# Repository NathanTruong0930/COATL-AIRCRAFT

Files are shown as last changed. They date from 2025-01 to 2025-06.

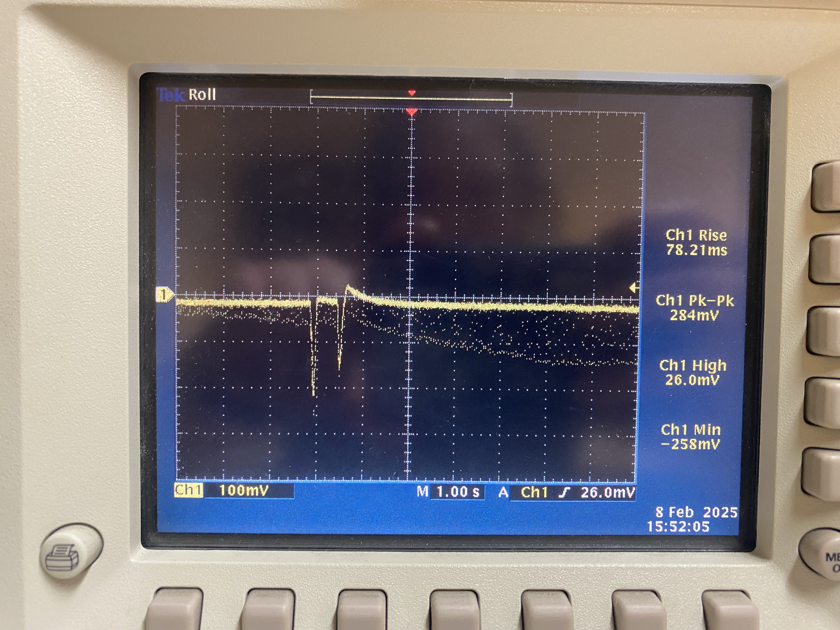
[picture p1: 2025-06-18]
Test Data/gain1_2chargesagain.jpg

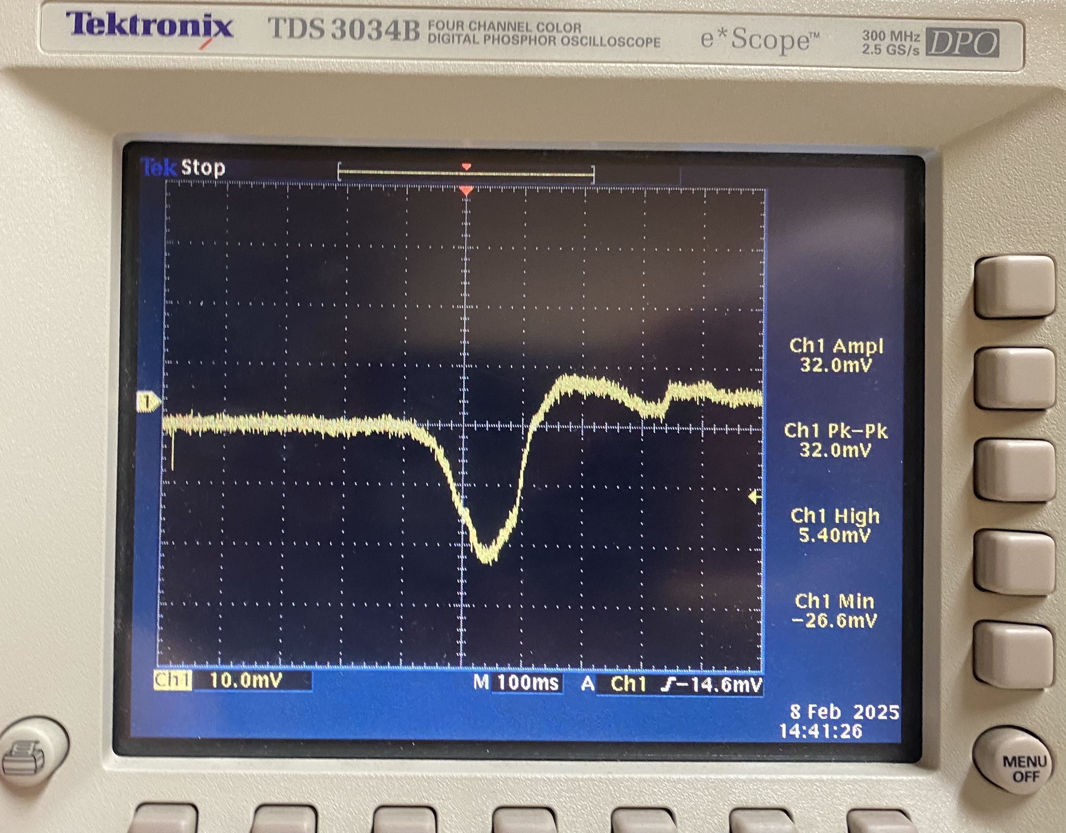
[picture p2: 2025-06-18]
Test Data/gain1_1charge_notcleanestpour.jpg

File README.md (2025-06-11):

# COATL-AIRCRAFT

## Team 3 Members:
- Felix Moss
- Annika Boyd
- Eisa Alsharifi
- Nathan Truong

---

### Project: Electrostatic Dust Analyzer

This repository contains code and resources for the **Electrostatic Dust Analyzer** project developed as part of the PSU Capstone program. This project utilizes a QT PY ESP32 Development Board to interpret current measurements taken from dust particles for use in determining air conditions. 

---

### Key Features

1. **Real-Time Detection of Charged Particles**

    Detects volcanic ash, mineral dust, and wildfire smoke using induced charge measurements.

2. **Electrostatic Sensing Technology**

    Uses a Faraday tube and wire electrodes to sense small electrical currents from passing particles.

3. **Wireless Data Transmission**

    The QT PY ESP32 Development Board transmits measurements via Wi-Fi to a web interface for real-time monitoring.

4. **Onboard Signal Processing**

    Calculates induced charge and estimates particle size based on charge density assumptions.

5. **Multi-Stage Gain Amplifier**

    Manually switchable gain stages (3.9×, 15×, 47×) allow for a wide range of signal amplitudes.

6. **Web Interface for Visualization**

    Displays live data including voltage, charge, gain level, and particle size.

7. **Compact, Low-Power Design**

    Operates on a 9V battery at ~1.35 W, suitable for eventual aircraft integration.

8. **Lab-Tested with Real Volcanic Ash**

    Validated through controlled experiments using Mt. St. Helens ash samples.

---

### Repository Overview

- **412_Practicum:** Assignments and other in class documents
- **Bill_of_Materials:** List of components used in the project
- **Fusion_Files:** PCB box fusion files
- **Gantt_Chart:** Project Gantt chart
- **Kicad:** All project KiCAD files
- **LTSpice_Simulation:** All LTSpice files
- **Research_Documents:** Documents and notes used for research purposes
- **Team_Meeting_Notes:** Notes from team meetings and discussions
- **Testing_Documentation:** Documentation of tests run by the team
- **Weekly_Progress_Report:** Weekly log of progress by the team

---

### Notes

- The files present in the **KiCAD** folder are of older designs and are not of the final PCB enclosure, which was provided by our sponsor Josh Méndez.
- 

---

### License:

This project is licensed under the [GPL-3.0 license](LICENSE).

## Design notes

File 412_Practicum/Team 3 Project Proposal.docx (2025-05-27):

# Capstone Project Proposals

TEAM-03 - COATL-AIRCRAFT

01/31/2025

Annika Boyd, Eisa Alsharifi, Felix Moss, Nathan Truong

REV #1

# 1. Executive Summary

Atmospheric particles like volcanic ash, mineral dust, and wildfire smoke can cause significant damage to aircrafts. These particles can clog components, erode turbine blades, and lead to engine failures, as seen by the 1982 British Airways Flight 009 incident. Not to mention, long term exposure to atmospheric dust in regions such as the Middle East leads to a much more rapid degradation of aircraft components.

This project aims to design and develop an electrostatic dust analyzer (EDA) that detects when an aircraft flies through a particle cloud. To do this the EDA will use the natural electrostatic properties of atmospheric dust to measure particle flow and size using induced currents on a set of wire electrodes. The small, low-power device will be mounted on the underside of the aircraft and operate continuously, monitoring the surrounding air. This will provide vital information for pilots, so as to help them respond accordingly and the EDA could offer helpful information about atmospheric dust trends.

Over the next six months, the project will deliver a working prototype capable of detecting particles within the size range of 50–500 microns and electrostatic charges of at least 10 fC. The final product will include hardware for signal digitization and software for real-time data processing.

# 2. Background and Research

- Sponsor

Josh Méndez is a researcher working at the intersection of engineering, materials science, geophysics, and planetary science. His work focuses on triboelectric charging. His research spans laboratory and field experiments to understand frictional charging and its effects, from volcanic lightning to planet formation. He also applies electrostatics and wireless sensor networks to study hazardous granular flows like volcanic plumes and wildfire smoke. Additionally, Dr. Méndez explores the science of coffee brewing, addressing multiphase problems and developing tools to enhance the brewing process.

- Technology Domain of Project

The project develops an Electrostatic Dust Analyzer (EDA) to detect airborne particle hazards like volcanic ash, dust, and wildfire smoke, which can damage aircraft engines. Using electrostatic sensing, the EDA measures charged particles in real time by detecting induced currents on wire electrodes. Mounted like a pitot tube, it provides continuous in-flight data to enhance pilot awareness and safety. The system complements existing aviation monitoring tools and contributes to long-term atmospheric dust analysis.

- How these Systems Work

Electrostatic dust analyzers (EDAs) work by detecting the natural charge on airborne particles. As an aircraft moves through the atmosphere, charged dust, ash, or smoke particles enter the sensor, which consists of wire electrodes positioned at the inlet and outlet of a narrow tube. When these particles pass through, they induce small electric currents on the electrodes. The system measures these currents to determine particle presence, charge, and potentially size.

- Previous Projects and Our Role

This project applies electrostatic sensing to detect airborne dust hazards in aviation, adapting a similar PSU graduate student project that uses a picoammeter to detect raindrops. Instead of raindrops, our system focuses on charged dust particles like volcanic ash and wildfire smoke, which can damage aircraft engines. Using a miniaturized Faraday cup, the sensor captures particles, and a picoammeter measures the induced currents to determine their presence and size. Unlike weather radar, which cannot detect fine dust, this system provides real-time monitoring to enhance pilot awareness and safety. The next steps include refining the Faraday cup design, developing the detection circuit, and testing sensitivity to ensure reliable airborne dust detection.

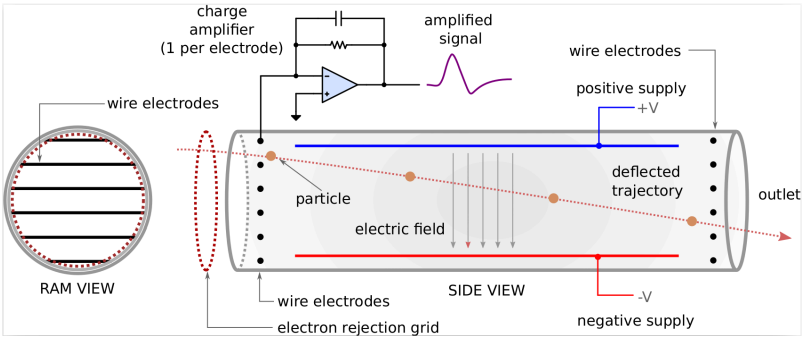
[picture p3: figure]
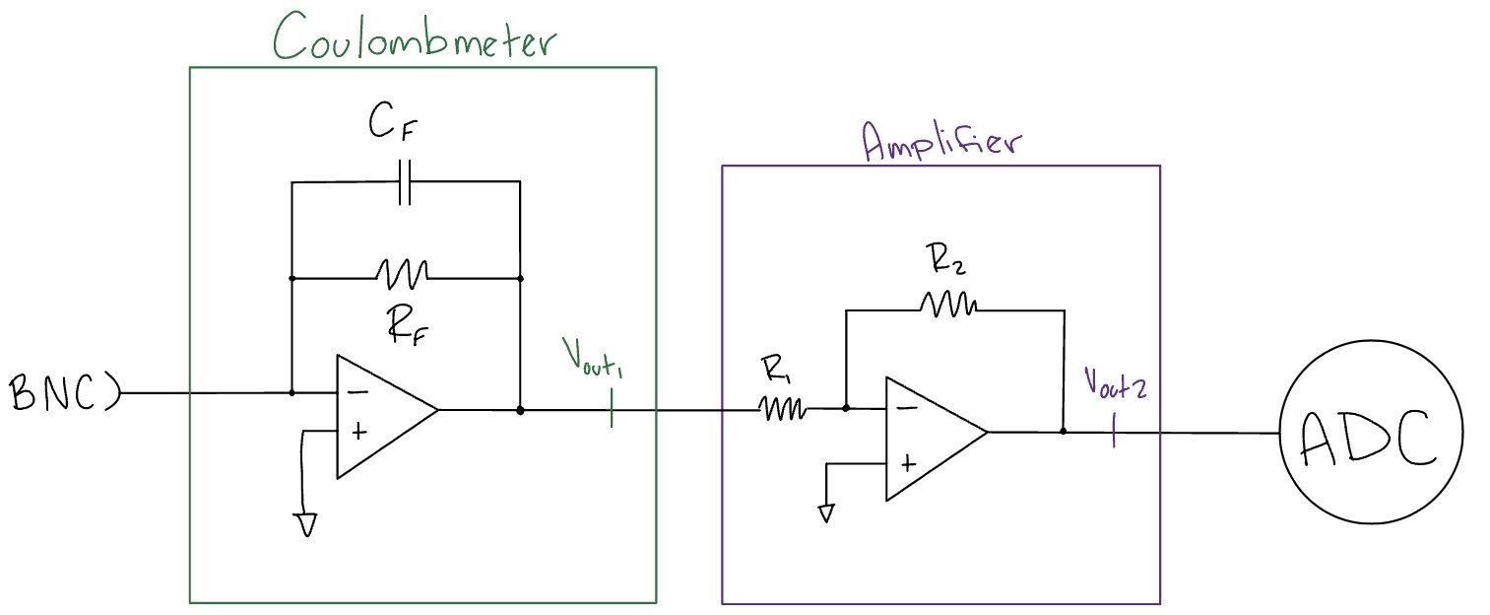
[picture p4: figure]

## Research

Currently, there is no commercial off-the-shelf project that can help with this project. The following articles were provided by our faculty advisor/sponsor:

- Low Level Measurements Handbook - 7th Edition

https://download.tek.com/document/LowLevelHandbook_7Ed.pdf

The first two chapters of the Low Level Measurements Handbook by Tektronix offer useful information for our electrostatic dust analyzer (EDA) project. Chapter 1 covers the challenges of measuring small signals and the importance of using the right equipment, like electrometers, coulombmeters, and picoammeters to measure very low voltages and currents. These instruments are essential for detecting the small charges created by airborne particles in our system. The chapter also emphasizes noise control, which will be crucial for maintaining measurement accuracy.

Chapter 2 focuses on the electrometer and ammeter. These tools are designed for precise low-level measurements, and the chapter provides us with the diagrams to build our own for measuring dust particles. Understanding how to use these tools effectively is key to ensuring our EDA can accurately detect charged particles in the atmosphere. Our EDA will need to be extremely sensitive to small charge variations caused by particles in the atmosphere, and the instruments and techniques discussed in these chapters guide our approach to achieving these measurements accurately. By understanding and applying the principles of noise reduction, precision measurement, and the correct use of instruments like electrometers, picoammeters, and SMUs, we ensure that the EDA provides reliable data for identifying particle hazards in the atmosphere.

- Embedded Electrostatic Sensors for Mars Exploration Missions

Embedded electrostatic sensors for Mars exploration missions (https://www.sciencedirect.com/science/article/abs/pii/S0304388604000488)

This article on embedded electrostatic sensors for Mars exploration is highly relevant to our project because it focuses on utilizing sensor technology to capture and analyze environmental data. While the project is specifically about measuring electrostatic fields on the Martian surface, the core principles and methods used in the project can be applied to our design.

Like the Mars sensors, we are developing sensors that detect and measure specific physical properties within a given environment. The emphasis on integrating sensors into a rover’s wheels for continuous data collection while the vehicle moves can directly inform our own sensor placement strategy. In our project, we are also integrating sensors into our device or system that allows for continuous measurement without interrupting the overall system.

Additionally, the electrostatic sensor technology used in the project provides useful insights on how to measure changes in environmental conditions (like surface charge or frictional effects), which may influence how we would capture similar changes in current. The use of materials selected for their triboelectric properties also highlights how material choice can influence sensor performance. This is an extremely important consideration for our project as we select components for maximum accuracy and durability.

While the context of the Mars project is different, the sensor development and environmental data analysis techniques show us valuable ideas on integrating sensors into systems to continuously monitor and analyze data in real-time, which is directly applicable to our EDA.

- Electrostatic Dust Analyzer for Dust Transport Measurements on the Lunar Surface

https://iopscience.iop.org/article/10.3847/PSJ/ad1ffe/pdf

This EDA is relevant to our team as we develop our own because the principles of electrostatics outlined here are key to understanding how dust particles interact with electric fields. Our device will use these interactions to detect airborne particles, making these concepts essential for ensuring accurate measurements in the complex environment around an airplane.

Their EDA project also highlights the importance of precise calibration and design in electrostatic systems. For our dust analyzer, we need to ensure it can accurately detect different types of particles under various conditions, such as turbulence and changes in temperature. Their techniques of sensitivity adjustment and shielding/grounding that were discussed in their report will help us fine-tune our system to achieve the right sensitivity and detection range.

Finally, the project covers how to reduce interference and improve system reliability. Our dust analyzer will work with highly responsive equipment, so minimizing noise and ensuring clear data is critical. The methods and underlying concepts in this project help us design a more reliable and effective device for detecting particle clouds in the environment around airplanes.

- NASA Patent for Mars Exploration Electrostatic Sensor

https://ntrs.nasa.gov/api/citations/20000058189/downloads/20000058189.pdf

The MECA/Electrometer patent has significantly informed our design and testing process for developing the electrostatic dust analyzer (EDA) to detect particle clouds around airplanes. Their use of triboelectric sensors gives us a potential option of integrating similar sensor arrays into our system to measure the electrostatic properties of particles in the air. By using materials with varying triboelectric properties, we can see how different particles interact with the electrostatic field. This allows us to select appropriate materials for our sensors and fine-tune the EDA’s sensitivity for particle detection. Additionally, the patent's detailed description of the guard ring and electrode array design shows the importance of minimizing interference from leakage currents, ensuring the measurements are accurate in all conditions.

The patent’s solid-state switching mechanism also gave us insights into improving the calibration and automation of our analyzer. The use of low-leakage solid-state switches to zero the instrument, as opposed to mechanical switches, has shown us a potential way to make the calibration process more precise. This is especially important for our system, which needs to operate consistently and with extreme precision in adverse environmental conditions. Overall, the techniques and innovations outlined in the patent have provided us with a good understanding of electrostatic measurement, as well as potential solutions that are directly applicable to our system's design and testing phase.

# 3. Product Design Specification

## Product Overview

- What is Our Product
  - The electrostatic dust analyzer (EDA) detects and measures airborne particles, such as mineral dust, volcanic ash and wildfire smoke, that pose risks to airplane safety. It continuously monitors the particle environment around an aircraft during flight, providing real time data on particle characteristics.
- How it Works
  - The EDA consists of an open-ended tube with wire electrode arrays at the entrance and exit. Charged particles induce currents on these electrodes as they flow through the tube. The system processes these currents using analog and digital signal processing hardware to infer particle size and charge. This data is then transmitted to a serial USB connection for viewing by the user.
- Potential Users
  - Users of this technology include commercial airline pilots, flight crews, aviation regulators, aircraft manufacturers, and atmospheric scientists (i.e. our sponsor Josh Mendez).
- Use Cases
  - For airline pilots and manufacturers, this device will greatly enhance safety and maintenance costs. Not only will this prevent pilots from flying for too long in particle-dense areas, it keeps the aircraft from being damaged, allowing for less to be spent on maintenance. As for science, the aggregated data from flights about atmospheric conditions is useful for observing atmospheric dust content.
- Project Delivery
  - The initial prototype will be developed and tested in a lab environment first. After validation, our sponsor will take the developed product to Mexico for use in testing and analysis of atmospheric conditions.
- How Users Utilize our Product
  - Pilots will be able to view real-time data regarding hazardous conditions in the air and react accordingly. Maintenance teams will be able to look at long term data collections that provide insight on when to schedule repairs or replacements. Scientists can view data logs from multiple flights and compare that new data with older information for further analysis.
  - In order to use the EDA, a compatible interface for storing the data coming from the EDA’s outputs is needed, as well as a power supply for the entire device.
- Product Life Cycle and Timeline
  - Lifecycle
    - The product should last around 10 years or so. Project development will last 6 months and be finished in July. Once completed, the device should be operational for approximately 10 years with periodic maintenance.
  - Timeline
    - 3 Months:
      - Development of circuit and physical design. Begin prototyping and testing.
    - 6 Months:
      - Product is fully functional after testing, validation, and refinement. Deliver to sponsor for use in experimentation.
    - 1 Year:
      - Product is used in experimentation at sponsor’s discretion
    - 2 Years+:
      - Product is subject to testing and regulatory approval. Device potentially becomes available for integration into aircraft fleets as a standard tool for aviation safety and atmospheric research.

## Stakeholders

- Team 3 Members
- Josh Méndez,
- COffee And Telesensing Lab at Portland State University

## Requirements

- Must
  - Device is able to detect particles
  - Device is sensitive to electrostatic charge
- Should
  - Low consumption of power
  - Small in size
  - Able to determine the size of particle

## Initial product design

- Hardware architecture
  - L0 and L1

L0 Block Diagram

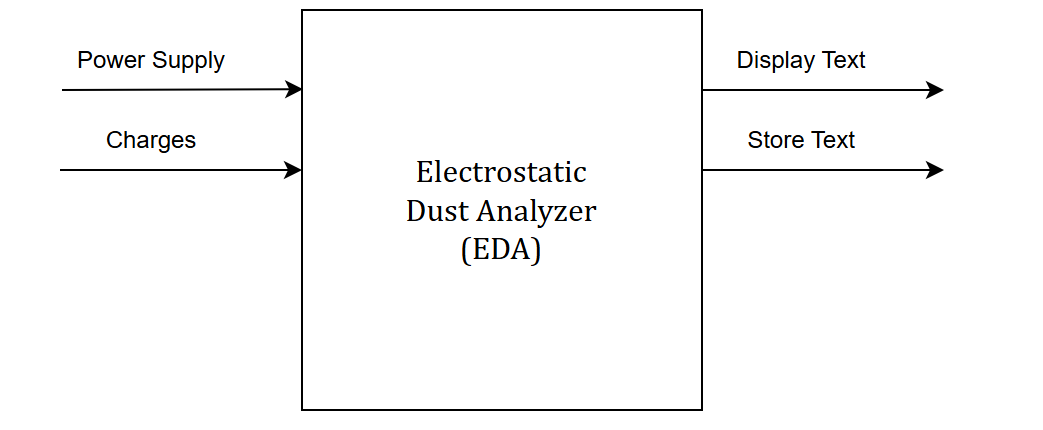
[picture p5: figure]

L1 Block Diagram

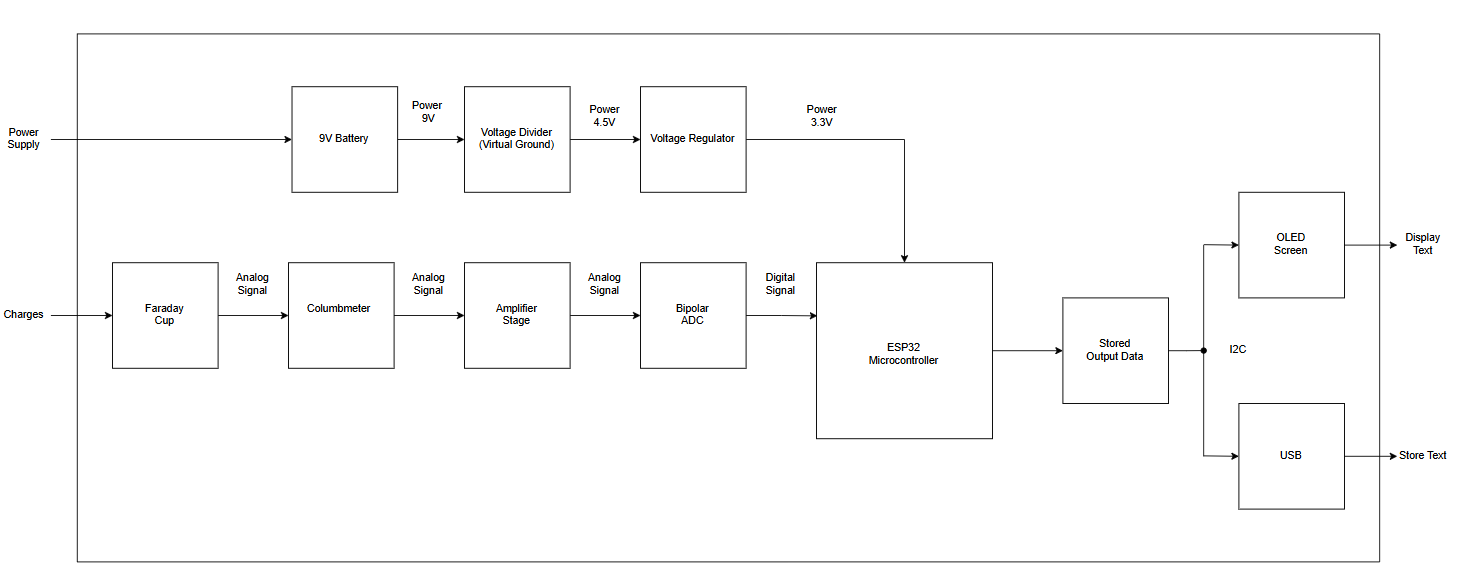
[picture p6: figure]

- Software Architecture
  - Programming Languages:
    - C/C++: Used for programming the microcontroller to control hardware components (e.g., ADC, amplifier, sensors) and implement data processing algorithms.Development Environments:
    - Arduino IDE: Popular for programming ESP32 due to simplicity and extensive library support, ideal for rapid development and testing
    - Git: To track version control and manage team contributions, and an easy way to share software files
- Data Flow in the Software
  - Data Collection:
    - The microcontroller receives digitized signals from the ADC, which represent the particle charges and sizes detected by the electrodes.
  - Data Processing:
    - Noise filtering through digital signal processing (DSP).
    - Converts ADC data to meaningful measurements, such as particle charge and size.
  - Decision Making:
    - The microcontroller evaluates the processed data to determine if a hazardous particle cloud is present. This may include checking thresholds for charge density or particle size.
  - Data Transmission:
    - The microcontroller sends results to the pilot interface using serial communication (USB or UART) for real time feedback or logging.
- User Interface / Experience
  - Pilot Experience:
    - Pilots receive real-time alerts on the cockpit’s OLED display about airborne particle concentration, allowing for immediate course adjustment to avoid hazardous zones, enhancing in-flight safety.
  - Research and Development Experience:
    - Researchers access detailed particulate data via USB for analysis facilitating ongoing improvement in predictive maintenance and environmental impact assessments.
- Other Considerations
  - Security
    - Physical Security:
      - The device will be mounted on the aircraft to keep it stable under flight conditions (such as turbulence, temperature changes, etc).
      - It will have a housing that will protect the electronics from moisture, dust, water, etc.
    - Electronic Security:
      - Shielding and grounding will be added to prevent electromagnetic interference (EMI) that could affect our EDA.
      - Insulation will be used to avoid short circuits and protect sensitive components from power surges.
    - Software Security:
      - Encryption for data transmitted over Wi-Fi or Bluetooth may be added if needed.
      - Maybe include password protection or some such to limit configuration changes to only those that need it.
  - Regulatory Compliance
    - Aviation Standards:
      - The EDA must comply with FAA and EASA regulations for airborne electronic equipment, including standards for electromagnetic compatibility (EMC) and safety.
      - The EDA’s design will consider DO-160 standards for environmental testing of airborne equipment, such as vibration, temperature, and pressure.
  - Radio Frequency Compliance:
    - If the device uses wireless communication (Wi-Fi or Bluetooth), it must comply with FCC standards for the US and NOM-208-SCFI-2016 standards for Mexico to make sure we have legal operation and certification in both areas.
    - The design will follow frequency band and output power limits to avoid interfering with other avionics systems.

## Verification plans

To make sure our system meets the project requirements and performs as expected, we will use the following testing strategy:

- Functional Testing
  - Test the ability of the electrodes to detect charged particles by introducing controlled particles with known sizes and charges (using shaken sand or volcanic ash).
  - Verify the coulomb meter accurately measures the charge induced by the particles (possibly a way to compare the charges with equipment in the lab).
- Signal Amplification and Conversion
  - Validate that the amplifier properly boosts the signal from the coulomb meter without significant distortion.
  - Confirm that the ADC correctly digitizes the amplified signals for the microcontroller.
- Data Processing and Transmission
  - Make sure the microcontroller processes the digitized data accurately and identifies the particle size/charge based on input signals.
  - Test the transmission of processed data to the pilot interface, hopefully under simulated flight conditions.
- System Integration Testing
  - Simulate particle clouds to test the full system, data flowing from the electrodes to the pilot interface.
  - Confirm that a sudden rise in particle counts triggers an alert or appropriate feedback for the pilot or at least displays correctly.
- Pass/Fail Criteria
  - The system must detect particles with diameters in the 50–500 micron range with charges of at least 10 fC.
  - The system should operate continuously without interruption during the test.
  - The output data must line up with known test particle parameters within an acceptable margin of error (maybe ±5% for size, ±10% for charge).
  - The pilot interface must receive data updates in real-time (or almost real time) without major delays.
- Documentation and Reporting
  - Record all test results systematically, including raw data, processed results, and any unexpected outcomes.
  - Provide proof of compliance with "must" requirements and note any areas for improvement before handoff to the industry sponsor.

## Risks

- Technical Risks
  - Electrode Sensitivity:
    - The electrodes may not detect particles with the required precision or sensitivity (50–500 microns and charges ≥10 fC).
      - Possible Solution: Have early experiments with controlled particle environments to check and deal with electrode sensitivity.
  - Signal Noise:
    - The amplified signal may include too much noise to accurately read our data.
      - Possible Solution: Using proper shielding and filtering to minimize noise in the circuit.
- Existential Risks
  - Time Constraints:
    - The project timeline may not allow enough iterations or testing to fully fix all issues with the system.
      - Possible Solution: Prioritize the main required functionality (particle detection and data transmission) and deal with secondary features later if necessary.
  - Budget Limitations:
    - The cost of components or unexpected expenses may exceed the budget.
      - Possible Solution: Select cost-effective components and think about trade-offs between performance and budget.
  - Communication Issues:
    - Data transmission to the pilot interface might not function correctly due to software bugs or hardware malfunctions.
      - Possible Solution: Test communication multiple times under simulated conditions.
- Critical Questions
  - How accurately can the system differentiate between particle sizes and charges?
  - Can the system process and transmit data quickly enough for real-time feedback?
  - Will the design function consistently in different environmental conditions, such as turbulence or extreme temperatures?
  - What calibration processes are required to ensure consistent performance, and how frequently must calibration be performed
- Unanswered Questions
  - The long term durability of the electrodes under continuous use is unknown due to limited testing time.
  - We might not fully verify how accurately the system handles unknown environmental particles.
- Back Up Plans
  - If Particle Detection Fails:
    - Simplify the system to detect only the presence or absence of charged particles without detailed size/charge analysis.
  - If Data Transmission Fails:
    - Store data locally on the microcontroller and provide pilots with a post-flight analysis instead of real-time feedback.
  - If Project Timeline Falls Short:
    - Deliver a partial system that demonstrates proof of concept for particle detection and signal processing, even if full integration is incomplete.
- Fallback Deliverable
  - At a minimum, the team will deliver a working prototype capable of detecting charged particles and outputting data for further analysis, even if full functionality (such as real time alerts) is not achieved.

## Deliverables

- Documentation
  - Project proposal
  - Weekly Progress Reports
  - Final report
  - Test plans
  - User Manual
- Hardware
  - A device capable of detecting particles with diameters in the range of 50-500 µm (must)
  - Detect charges of at least 10 fC (must)
  - Digitize the analog signals (should)
  - A software to measure the particle size (should)
- Software
  - Using a microcontroller, the software and firmware is published on Git to properly operate and re-design the EDA using Git
  - A way to send all the data acquired to another device or server
- Presentation
  - Weekly or bi-weekly meetings with the sponsor
  - ECE Capstone Poster Session poster
- Delivery Method
  - Digital content: all digital files, including software, documentation, CAD design, and 3D print design to the team’s dedicated Git repository
  - Physical contents: all functioning prototypes and the final working product will be delivered to the sponsor

# 4. Project Management Plan

## Timeline, with milestones

- Gantt Chart
  - Team 3 Gantt Chart (https://docs.google.com/spreadsheets/d/1_7xgBOEVhSrhBdYwNqpK6ZXGdGlyBkKYaVhsfQWFYbA/edit?usp=sharing)
- Timeline Milestones
  - End of Week 3:
    - Research phase completed, project proposal submitted.
  - End of Week 6:
    - Initial design finalized.
  - End of Week 10:
    - First working prototype ready.
  - End of Week 14:
    - Testing phase completed with feedback.
  - End of Week 17:
    - Second prototype refined and verified.
  - End of Week 20:
    - Final project delivered.

## Budget and Resources

Our team’s budget is approximately $1000. The allocated budget will cover circuit parts, PCBs machining materials, and potentially 3D print plastics during the design, prototyping, testing, and refinement phases of development.

For workspace, we will be using both the Capstone Lab and the MME Manufacturing Lab along with room 085-03 as the main meeting hub. Additionally, we may use the EPL as a resource for 3D printing or acquiring circuit parts.

## Intellectual Property Discussion

The IP for this project is in the public domain. The design, implementation, and results of this project are freely available for public use, distribution, modification, and reproduction without requiring permission or payment.

## Team

- Felix Moss:
  - Strengths: Schematic and PCB design, group documentation/management, soldering.
  - Areas of Practice: 3D printing, machining, analog-to-digital circuitry, op-amps.
  - Role: Group documenting, physical designing, validation
- Eisa Alsharifi:
  - Strengths: Schematic, PCB layouts, C programming, soldering, BOM/ tracking expenditure
  - Areas of Practice: 3D design, op-amps, analog-to-digital conversion.
  - Role: Circuit designing, validation, BOM/ordering
- Annika Boyd:
  - Strengths: Schematic design, soldering, hardware debugging.
  - Areas of Practice: 3D design, machining, analog design.
  - Role: Circuit design, validation
- Nathan Truong:
  - Strengths: Circuit design, prototyping, hardware debugging, data analysis.
  - Areas of Practice: Analog design, op-amps, 3D design.
  - Role: Physical designing, validation

## Development Tools and Process

- Our team is splitting the work up into six phases: Planning, Design, Prototyping, Testing, Refinement, and Finalizing. Time during each phase will be dedicated explicitly to completing the goals outlined in the Gantt chart.
- For collaboration, we are using Discord, Git, Google Drive, and Email.
- For technical tools, we will be using KiCAD, LTSpice, Arduino IDE in C, and Fusion 360.

## Acceptance and Sign-Off

This section serves to confirm that the undersigned faculty advisor and industry sponsor have reviewed the content of this project proposal and agree with the plan laid out herein for the Capstone Project, COATL-AIRCRAFT. The undersigned acknowledge that the proposal meets the necessary criteria and that they support the project’s objectives, methodology, and timeline as documented.

This acceptance also verifies that the faculty advisor and industry sponsor commit to providing the necessary oversight, support, and resources to ensure the project’s successful completion as envisioned.

Faculty Advisor & Industry Sponsor:

Name: Joshua Mendez

Signature:

Date: 1-Feb-2025

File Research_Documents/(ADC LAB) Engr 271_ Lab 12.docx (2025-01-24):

Annika Boyd

6/1/2023

ENGR 271: Digital Logic Design

# Lab 12: Analog-to-Digital Conversion (ADC)

## Introduction

In this lab, we focused on simulating and understanding two types of analog-to-digital converters. The two types we focused on were the flash ADC and the successive approximation register (SAR) ADC. Learning about these ADCs is important for an electrical engineering student because ADCs play an important role in converting analog to digital signals. This would also be super useful for future projects as an engineer and it provides a solid foundation for dealing with coursework and real-world challenges related to signal processing, system design, and optimization.

## Part A: Flash ADC

1. In this step, we used Multisim to create the flash ADC given and tested the circuit to ensure that it worked by creating a table.

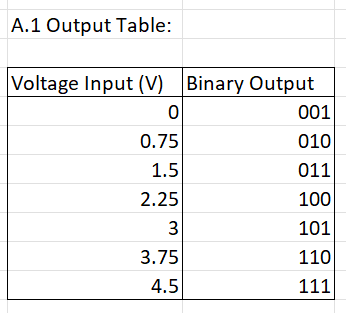
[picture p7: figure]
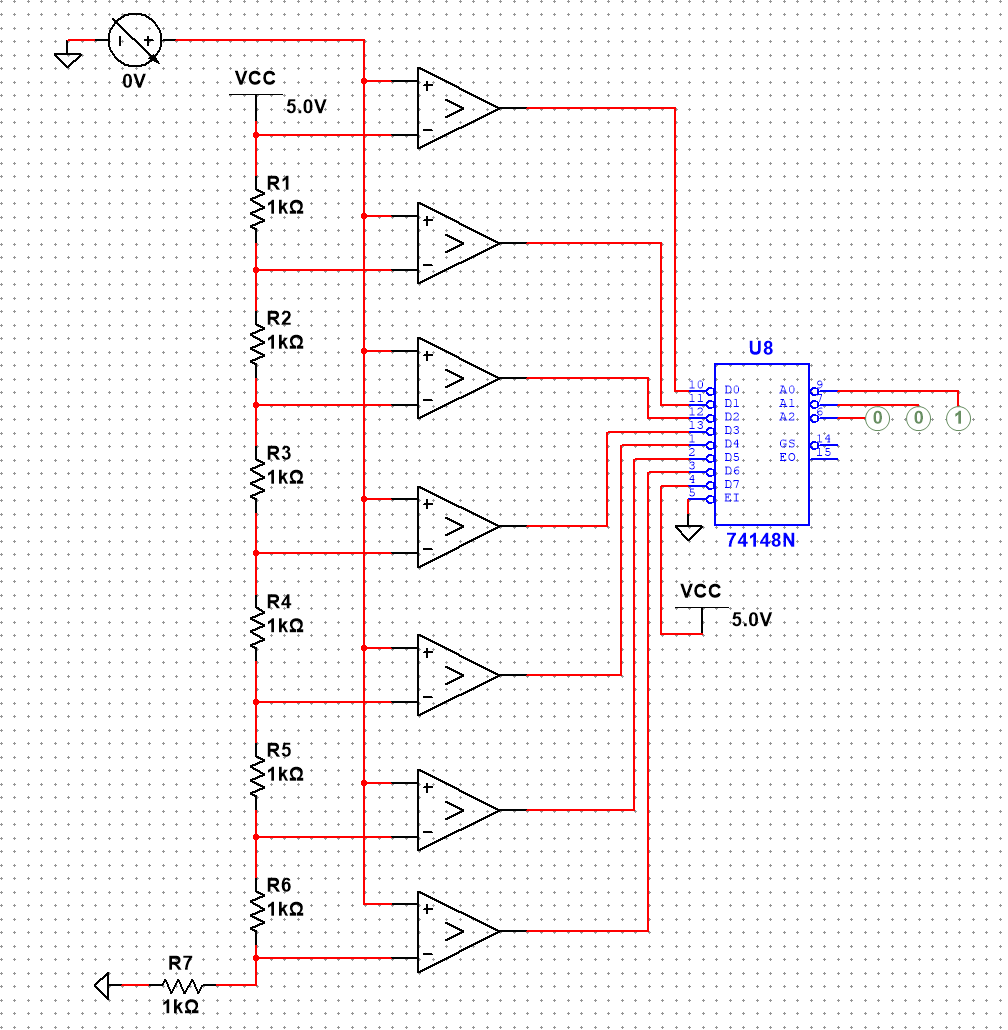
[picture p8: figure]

2. In this step, we used datasheets for the components to calculate how fast the flash ADC. From the data sheet, the propagation delay for the LM339 comparator is 15ns and the delay for the 74148 encoder is 10ns. Therefore, the total delay for the flash ADC is the sum of both, being 25 ns. Now, we know that frequency is the inverse of time, so we apply that here and find that the frequency is 40 MHz. Meaning that the speed of the flash ADC is 40MHz.
3. In a flash ADC, the component count grows as the number of bits increases. Specifically, the comparator component increases by a factor of 2n - 1, and the resistor component increases by a factor of 2^n, where n represents the number of bits. Consequently, as the number of bits rises, the physical size of the ADC chip must expand exponentially. This growth in size directly impacts the cost of manufacturing the flash ADC.

In the flash ADC, the amount of space required on silicon increases two times the number of bits increased by. This is due to the fact that the input voltage is compared to a set of reference voltages generated by a resistor ladder network.

4. In this procedure, we had to design logic for each pair of neighboring comparators that prevents bubble errors (non-thermometer code) from being sent to the priority encoder. To prevent the bubble errors, we realized we had to add AND gates after the comparators, with the exception of the last one. Below are multiple screenshots of the circuit working in multisim.

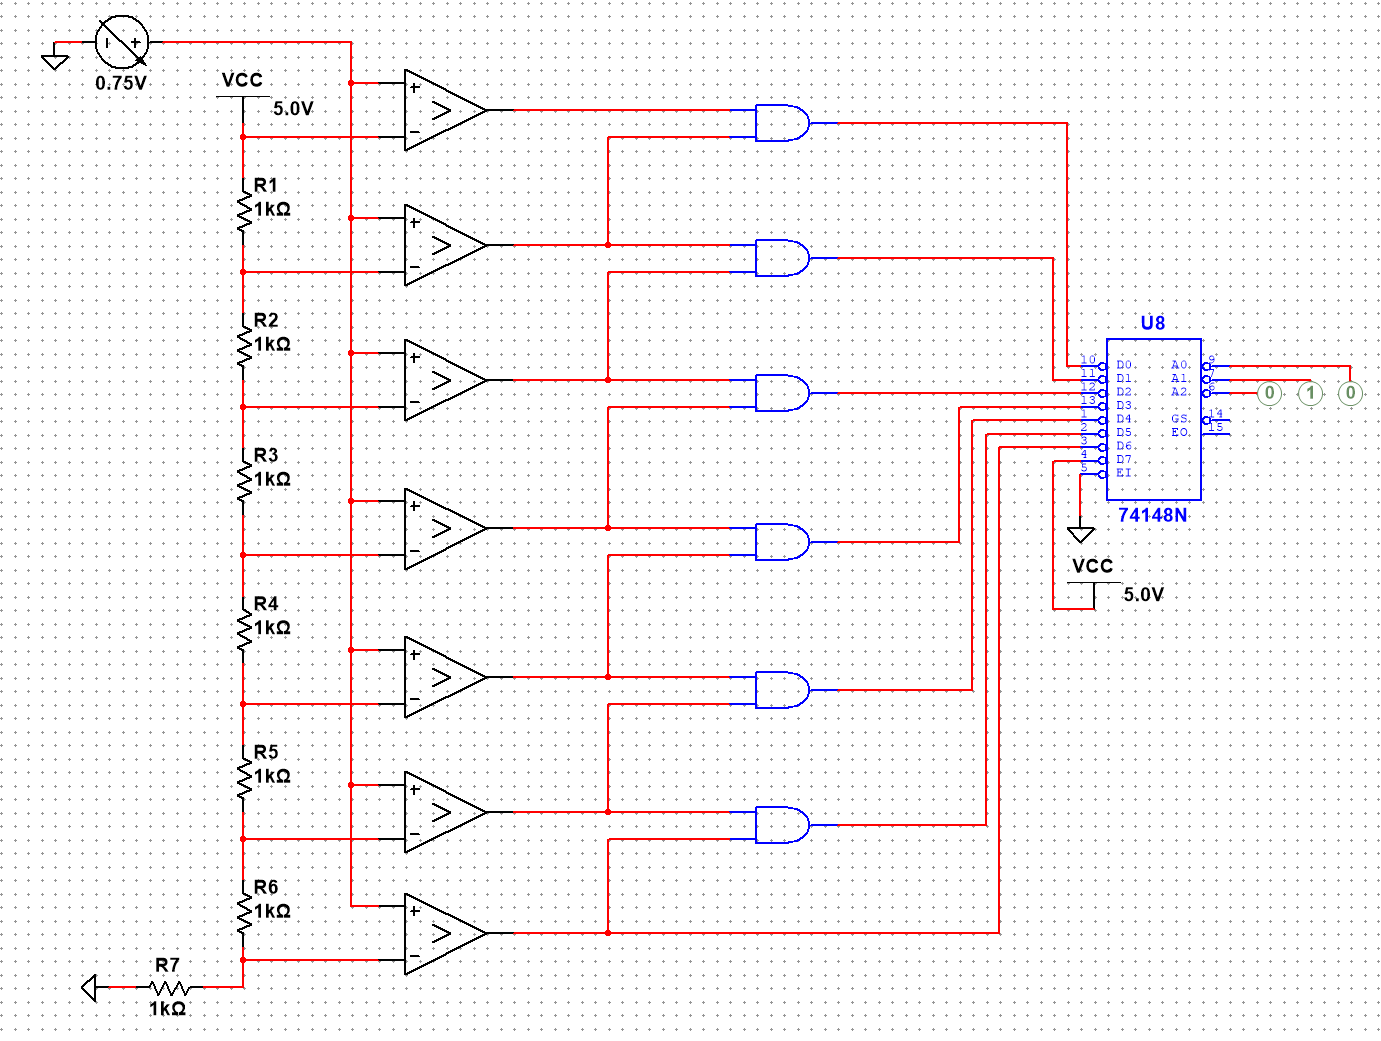
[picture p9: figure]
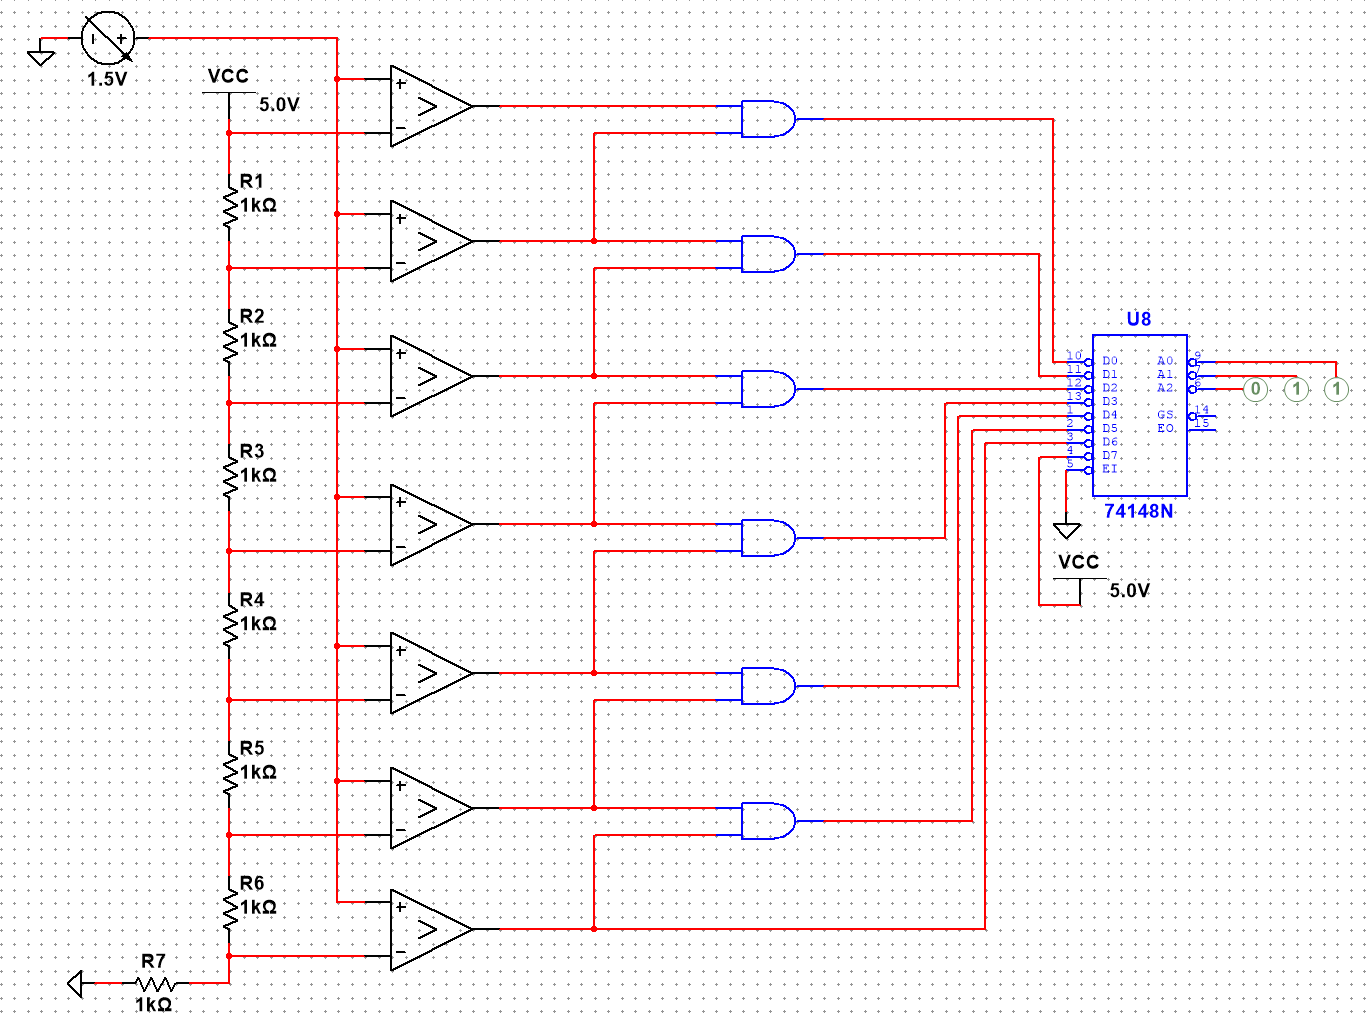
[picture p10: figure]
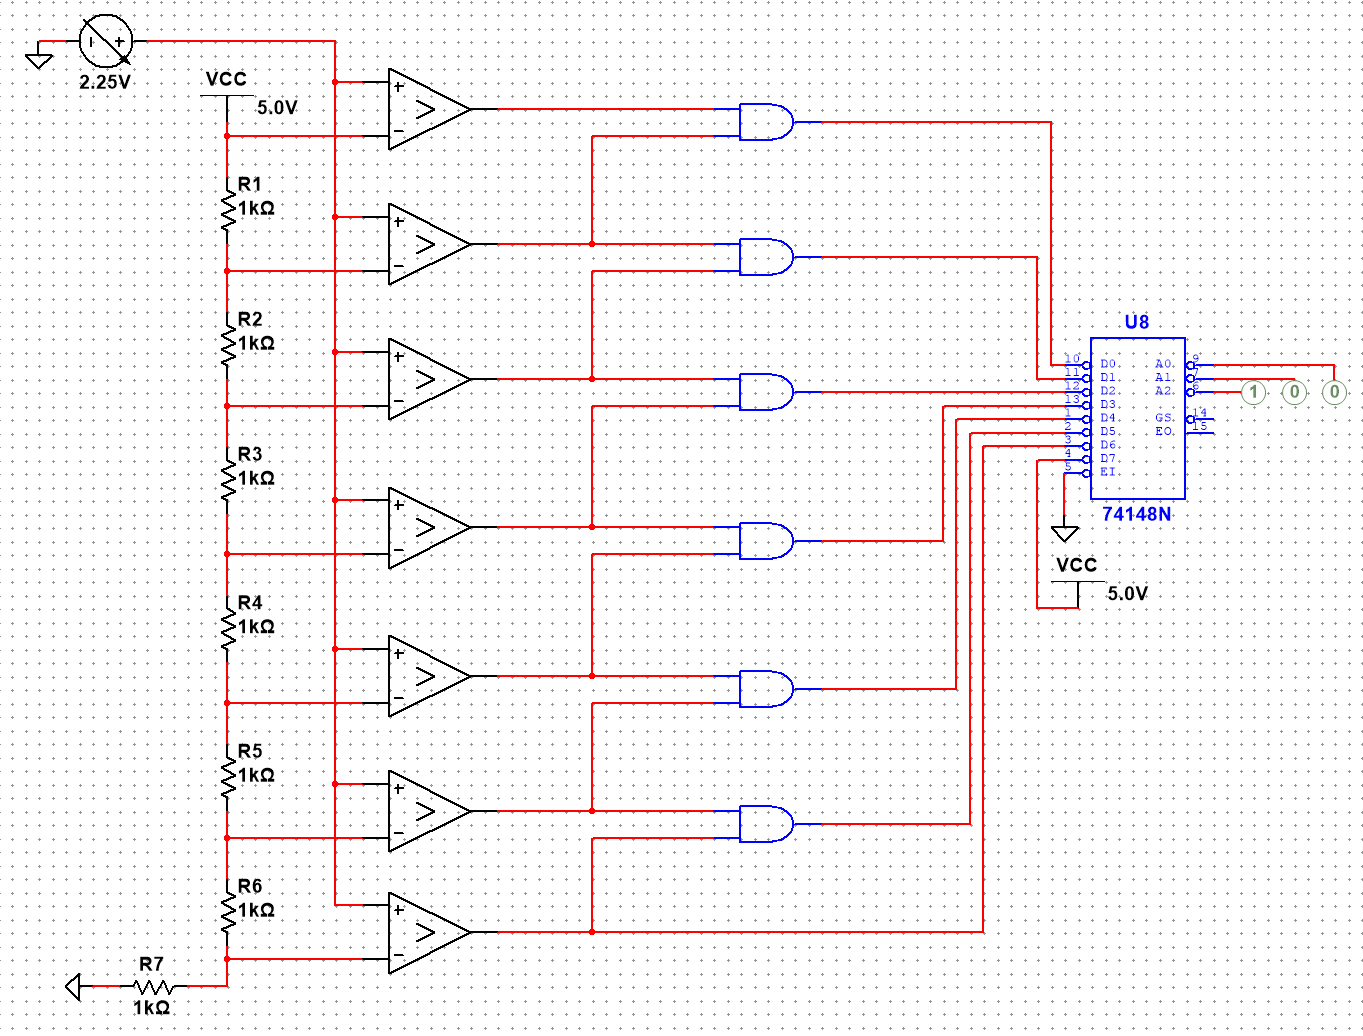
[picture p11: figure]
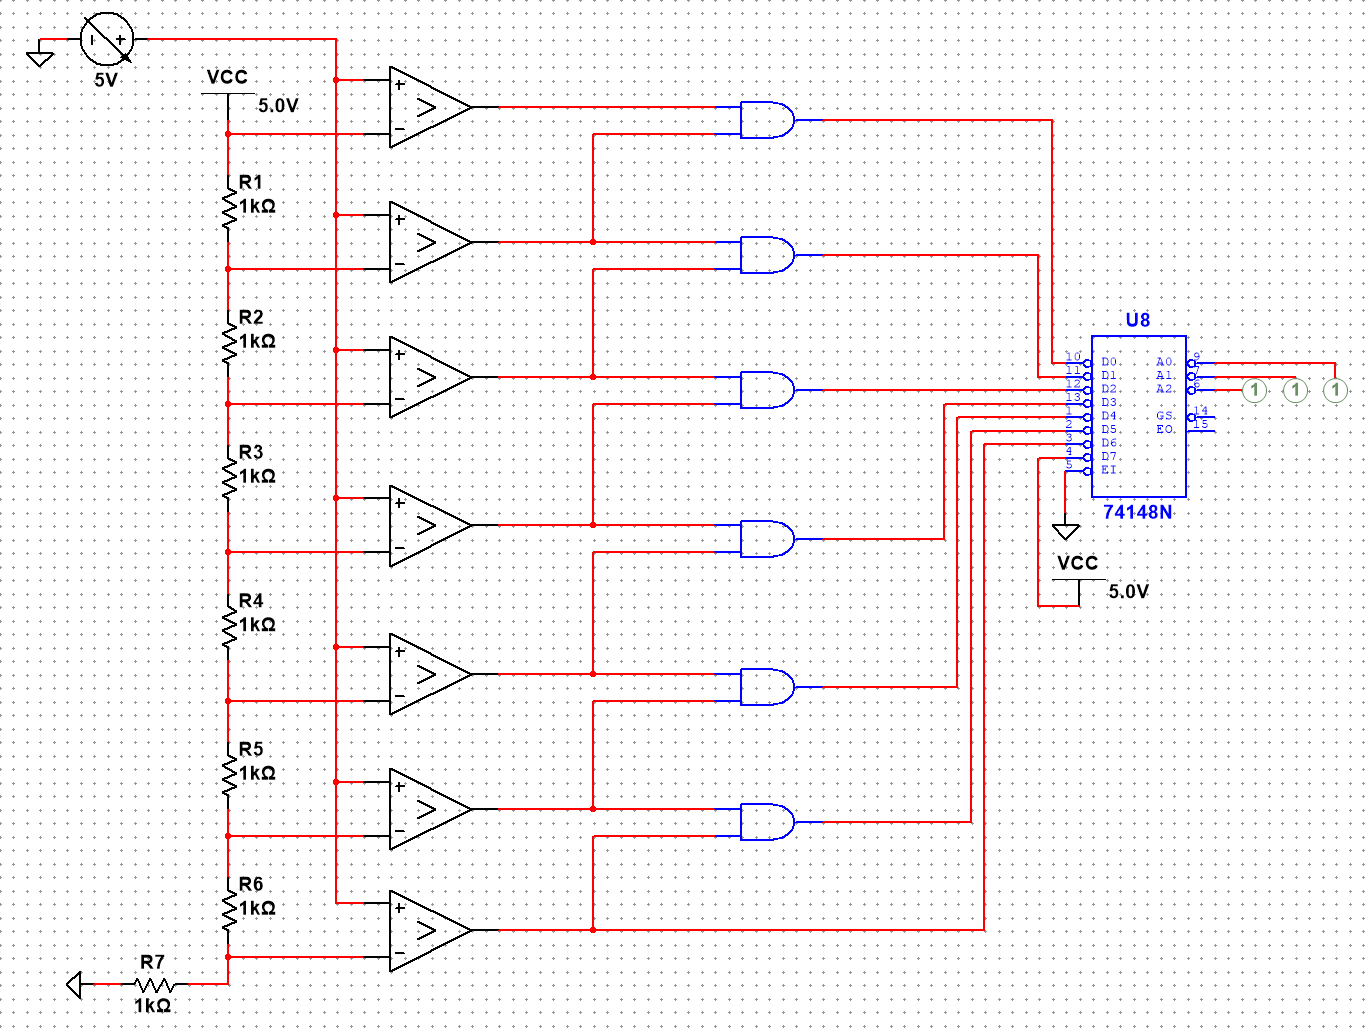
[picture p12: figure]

## Part B: Successive Approximation Register (SAR) ADC

5. In this step, we built the given SAR ADC in multisim and tested the circuit with multiple values. We chose the first two cases to be a 0v case and a 5v case because they are edge cases and that is often where errors appear. Next we chose the same value as the example given to ensure that the circuit was working correctly. The next cases were at 2.25v and 3.75v because we thought it would be a good idea to show more of the cases in the middle, as they weren’t super represented.

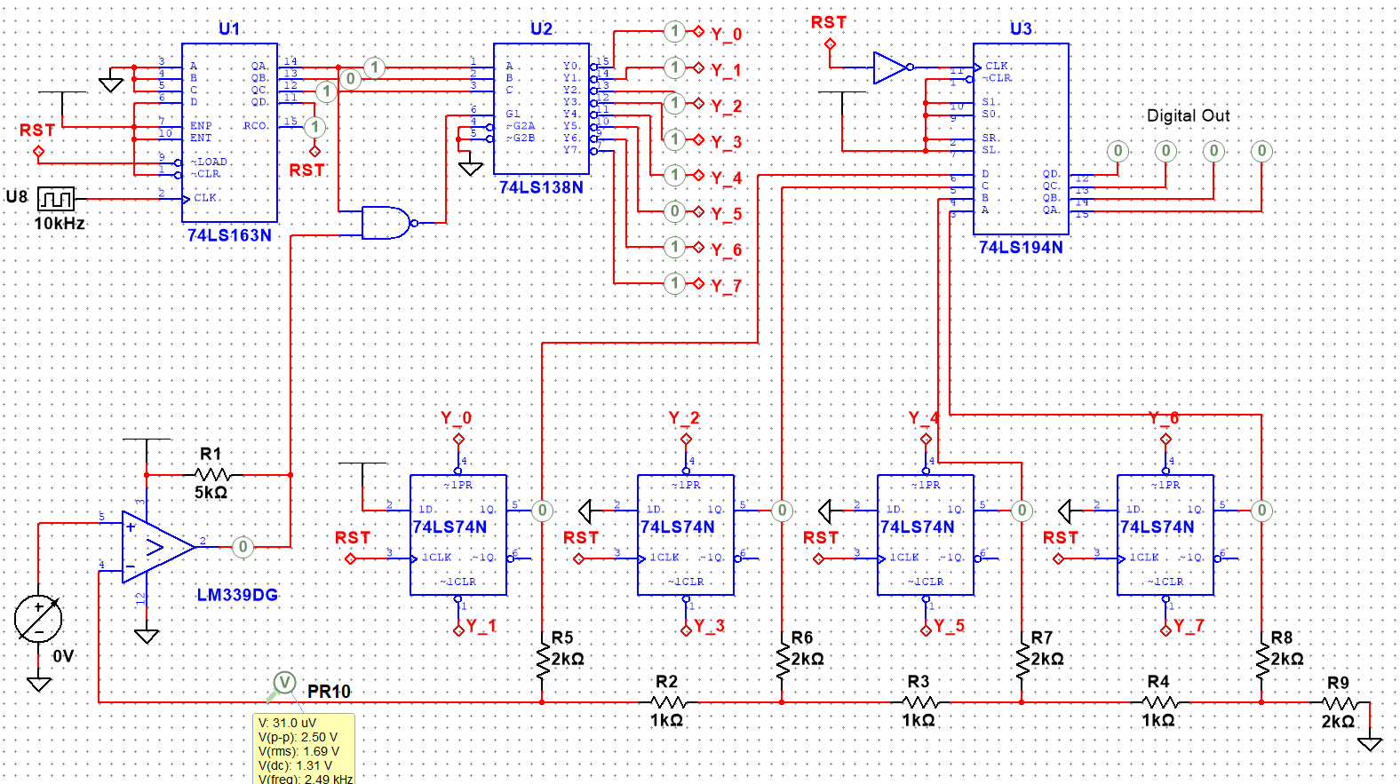
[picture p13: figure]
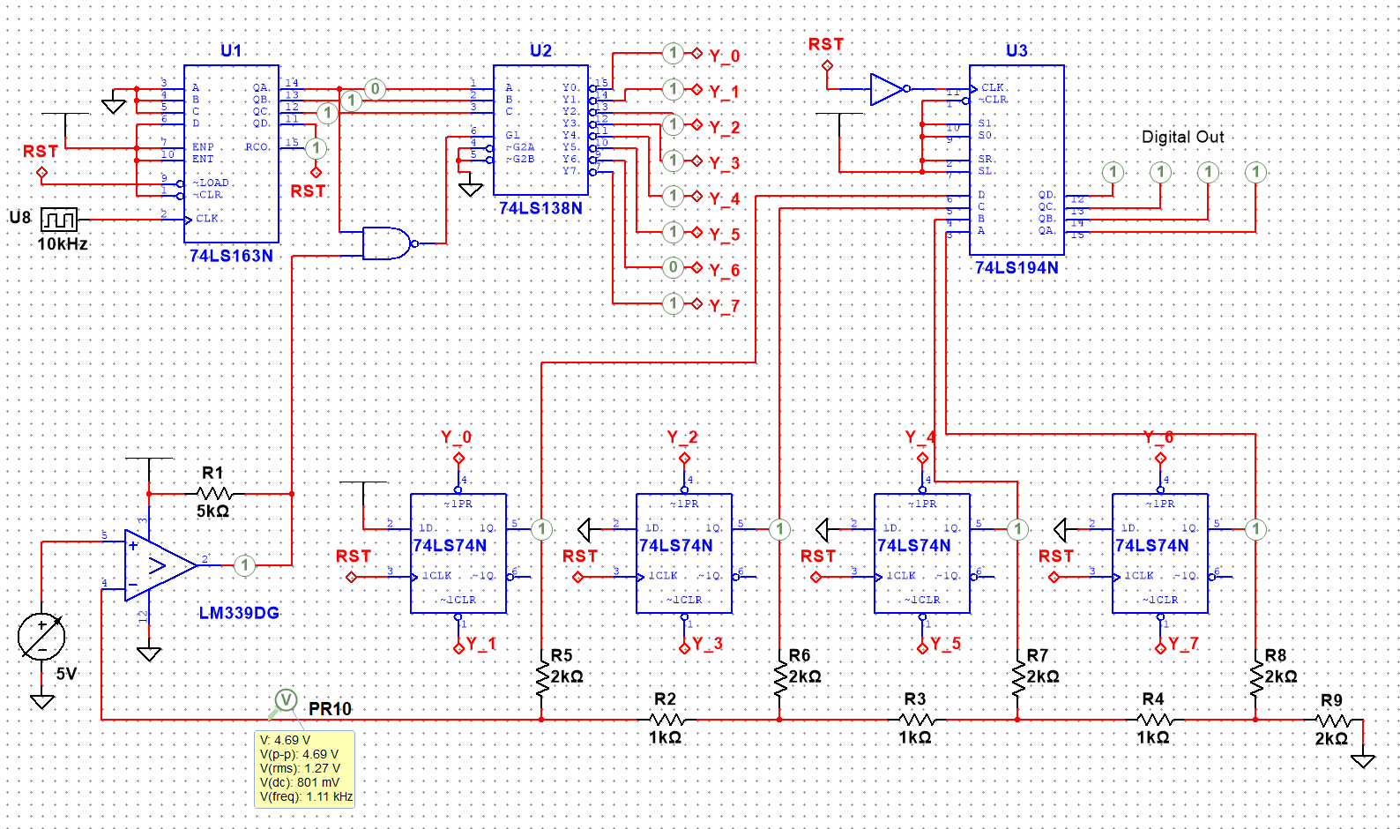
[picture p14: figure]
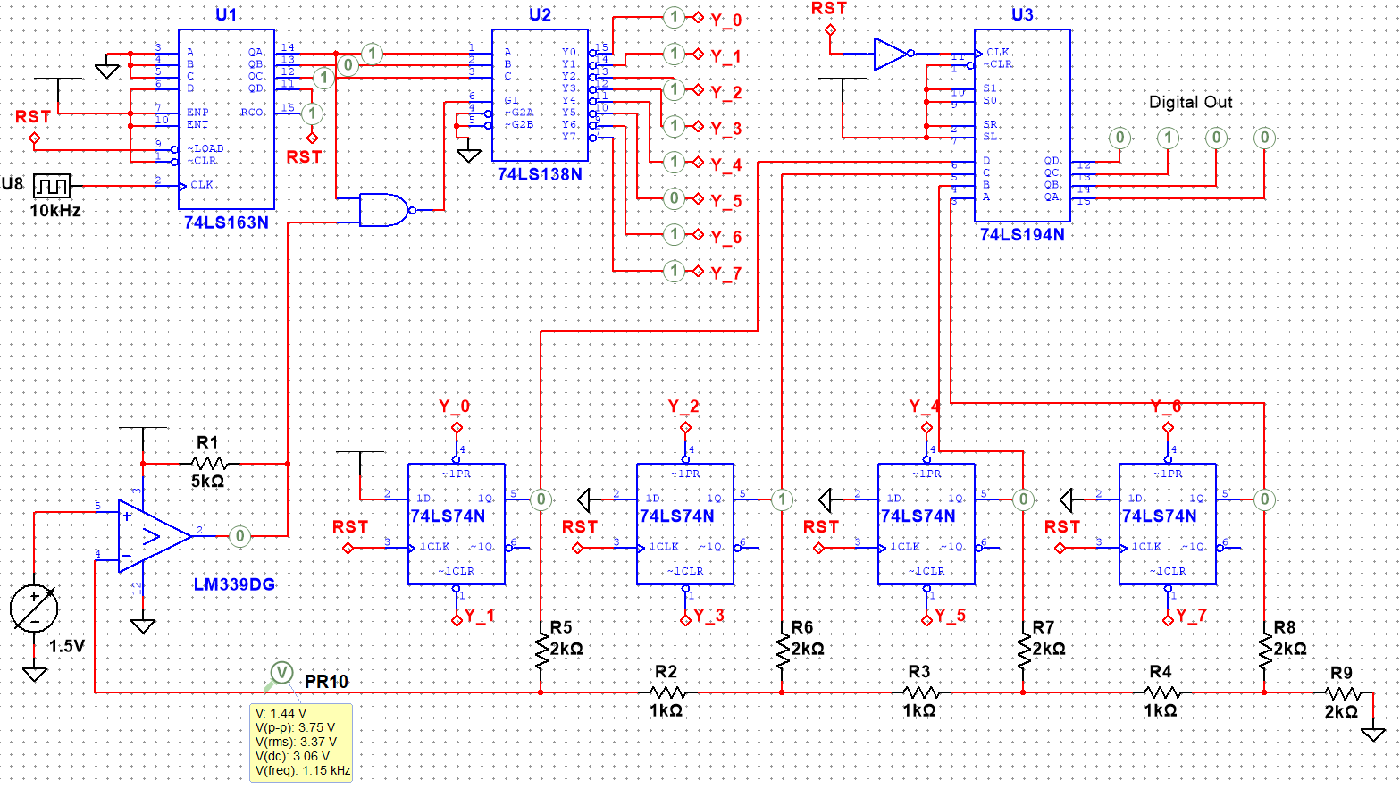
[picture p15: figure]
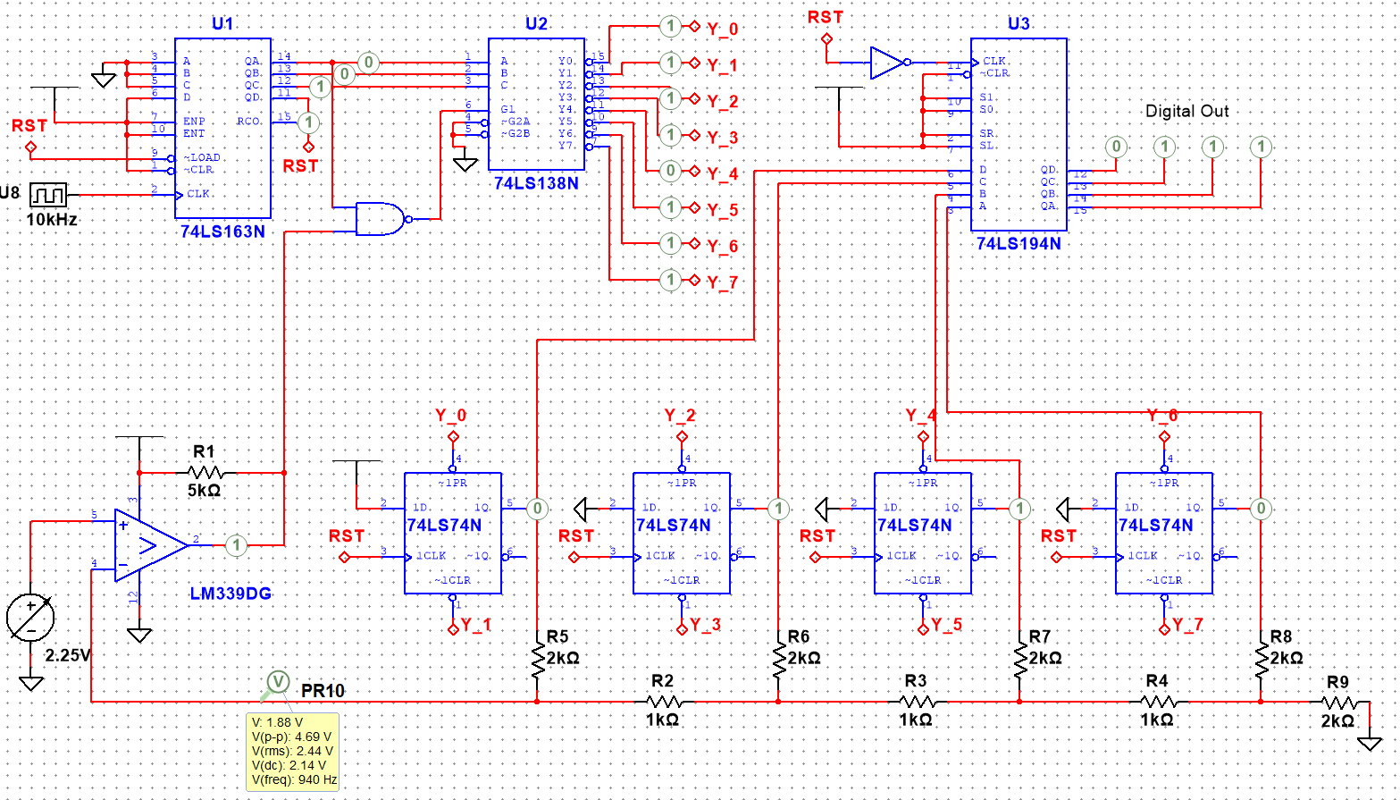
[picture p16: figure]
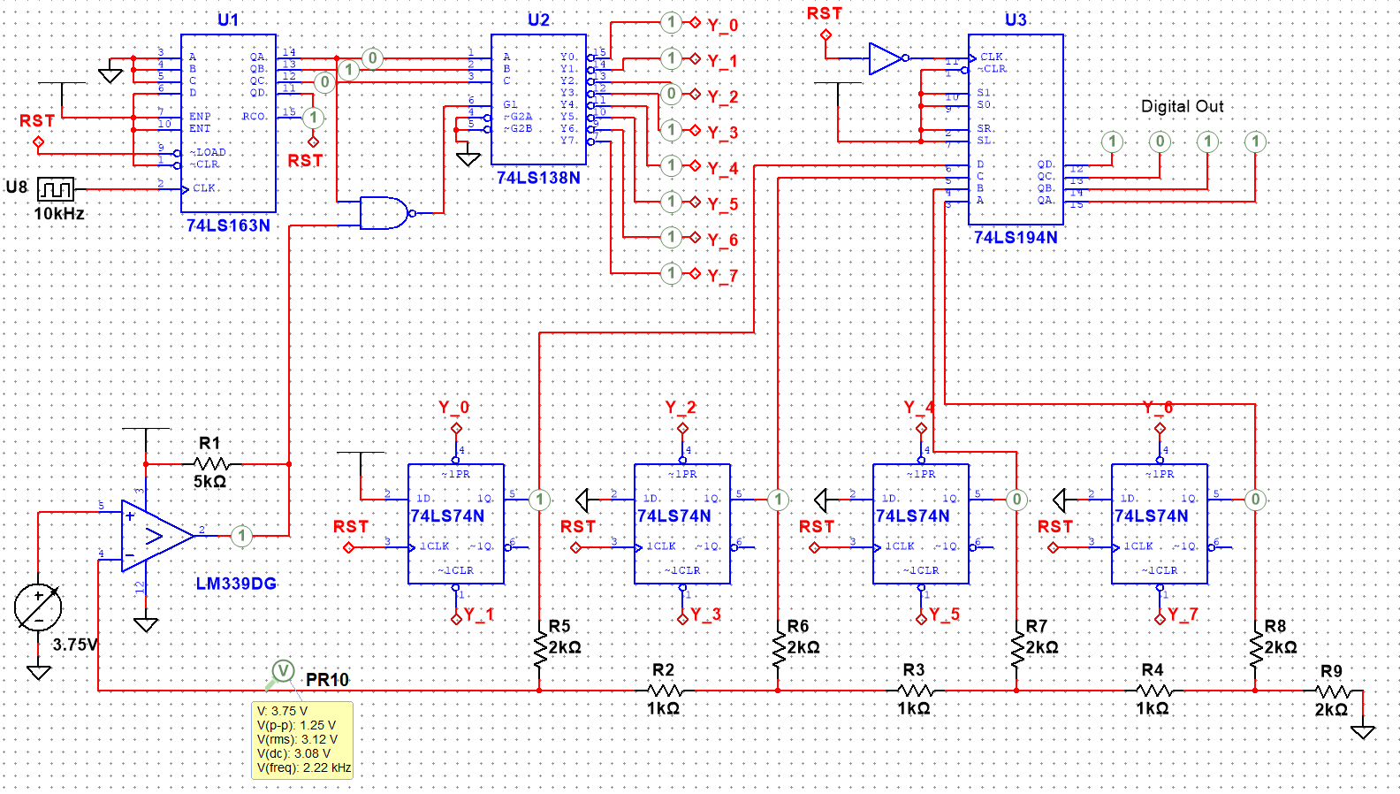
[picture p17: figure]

6. In this step, we had to draw a timing diagram for the 74163 IC that showed the CLK, QA, QB, QC and RST signals. This can be seen below, where we also see that the number sequence it is configured to produce is 8-15.

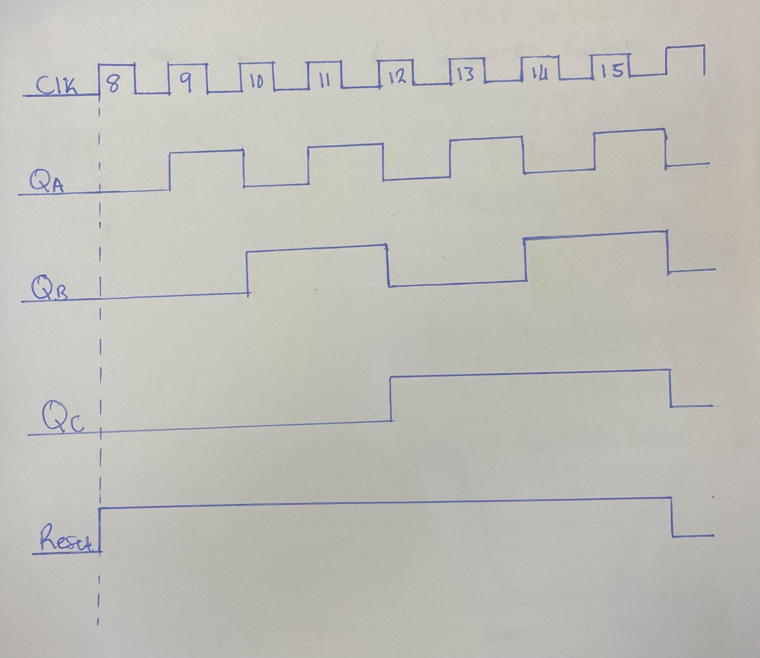
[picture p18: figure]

7. The SAR ADC is initialized by configuring the necessary control registers and setting the conversion start. The circuit incorporates a 74163 counter IC to analyze the analog input and generate a digital number at its output. The output from the 74163 is then fed into a 74138 decoder, which produces an 8-bit output based on the 4-bit counter output.

Upon conversion start, the SAR ADC sets the Most Significant Bit (MSB) of the digital output to '1' and sets the remaining bits to '0'. The initial state, Y0, generates an output of 1000 from the D flip flops. Subsequently, Y1 sets the next flip flop, while Y3 potentially clears it. This cycle continues, setting and potentially clearing each bit in the SAR ADC.

The SAR ADC operates in two stages: the setup stage, where each bit is initially set to '1', and the decision stage, which determines whether a bit should be cleared or retained. The decision is made by the comparator, which outputs '1' if the DAC output exceeds the input voltage, and '0' otherwise. Once the conversion restarts, the D flip flops hold the values and transmit them to the 74194, which stores the final value.

Based on the output of the comparator, the SAR ADC determines whether the current approximation is higher or lower than the input voltage. If the comparator output is '1', indicating that the current approximation is higher, the corresponding bit remains set, and the SAR ADC moves to the next lower significant bit.

8. A flash ADC, also known as a parallel ADC or parallel comparator ADC, is an ADC that directly converts analog input voltage into a digital output using voltage comparators. It provides high resolution and good linearity due to the direct mapping of voltage levels to digital outputs, making it suitable for applications that require accurate and linear conversion. However, flash ADCs have limitations such as higher component count, increased power consumption, and higher manufacturing costs compared to SAR ADC architectures. They are also susceptible to mismatches and errors in the comparator network, requiring careful design techniques to mitigate these effects.

On the other hand, a SAR ADC uses a successive approximation algorithm to convert analog input voltage into a digital output. SAR ADCs offer good resolution, moderate conversion speed, and relatively low power consumption compared to the high-speed ADCs like the flash ADC. However, SAR ADCs have slower conversion times since the successive approximation algorithm requires multiple iterations for accurate approximation of the input voltage. SAR ADCs also feature more complex circuitry, including a DAC and a comparator, along with the need for a precise reference voltage source. Nonetheless, SAR ADCs retain a balance between resolution, speed, and power consumption, making them commonly used and handy in many different applications.

## Conclusion

In conclusion, this lab provided helpful knowledge about two important types of analog-to-digital converters: the flash ADC and the SAR ADC. The flash ADC offers high resolution and good linearity, but comes with increased component count, power consumption, and manufacturing costs. On the other hand, the SAR ADC has a better balance between resolution, speed, and power consumption, making it a good choice for various applications. If we continued with the themes of this lab, I would say we should either learn about more types of ADCs or look into different areas in the real world where these ADCs are used and for what purposes.

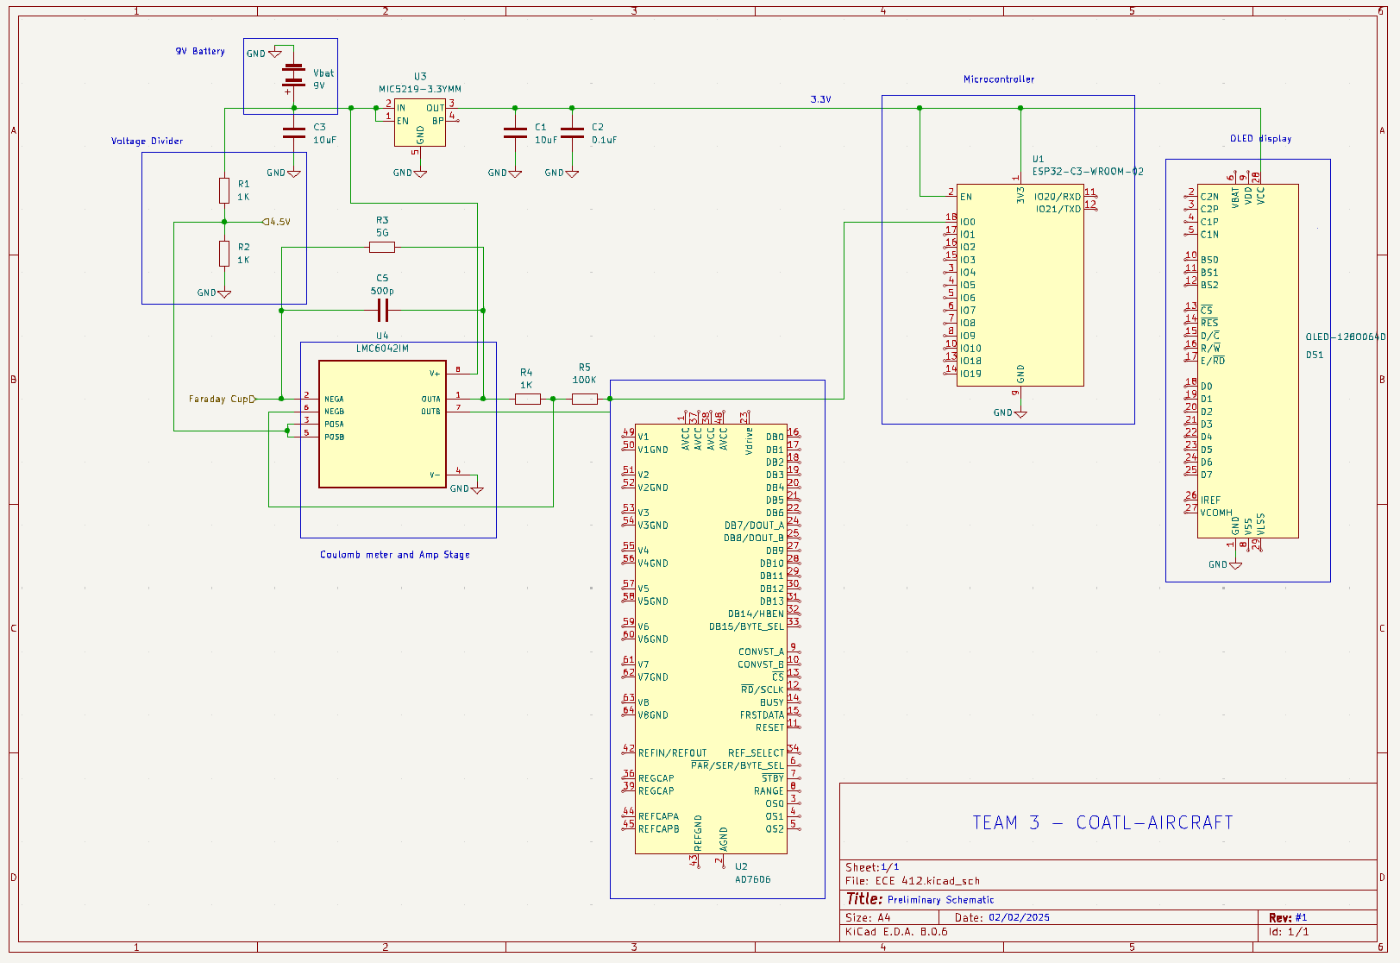
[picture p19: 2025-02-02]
Schematic/Screenshot 2025-02-02 145736.png

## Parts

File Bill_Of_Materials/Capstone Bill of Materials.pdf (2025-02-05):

Bill Of Materials for: Team 3 COATL Aircraft Sensor
Last modified: 2/5/25
PCB version: N/A
BOM revision: 1.1 | P/NP = Place/Not Place (components marked NP are not stuffed on the board)
Cnt | Part References | P/NP Mfg | Mfg PN | Description | Dist | Dist Part Number | Cost Ea. | Cost Total
3 | P | Texas Instruments | LMC6042IM/NOPB | Dual 15.5-V 100-kHz operational amplifier | Mouser | 926-LMC6042IM/NOPB | $2.75 | $8.25
3 | P | Texas Instruments | LMC6081IMX/NOPB | Prec CMOS Sgl Op Amp | Mouser | 926-LMC6081IMX/NOPB | $3.07 | $9.21
2 | P | KOA Speer | SM102035007FE | 5000M ohms ±1% resistor | Mouser | 588-SM102035007FE | $5.58 | $11.16
TOTAL: | $28.62

VERSION INFO

Rev | Date | Notes
1.0r1 2025-02-05 | First order of parts
1.0r0 2025-01-19 | Initial BOM. Not everything chosen, still need to finish shematic

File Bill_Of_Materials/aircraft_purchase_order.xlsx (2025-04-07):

 | Item Description | Catalog # | Unit (example: case, each, package) | Quantity | Amount per Unit | Item Total
1 | Thick Film Resistors - SMD 10 kOhms 250mW 0805 1% AEC-Q200 Double Power Version | 603-AC0805FR-7W10KL | 0805 SMD | 15 | $0.024 | $0.36 | 2025-04-06
2 | Thick Film Resistors - SMD 39 kOhms 125 mW 0805 1% | 603-RC0805FR-0739KL | 0805 SMD | 10 | $0.012 | $0.12
3 | Thick Film Resistors - SMD 150 kOhms 250 mW 0805 1% | 603-RC0805FR-13150KL | 0805 SMD | 10 | $0.012 | $0.12
4 | Thick Film Resistors - SMD 470 kOhms 125 mW 080 5 1% | 603-RC0805FR-07470KL | 0805 SMD | 10 | $0.012 | $0.12
5 | Multilayer Ceramic Capacitors MLCC - SMD/SMT 50V 0.1uF X7R 1206 10% | 80-C1206C104K5RACLR | 1206 SMD | 50 | $0.054 | $2.70
6 | Multilayer Ceramic Capacitors MLCC - SMD/SMT 1.0uF +-10% 25V | 791-1206B105K250CT | 1206 SMD | 15 | $0.065 | $0.98
7 | Multilayer Ceramic Capacitors MLCC - SMD/SMT 10uF+/-10% 25V X7R 3 1206 | 187-CL31B106KAHNNNE | 1206 SMD | 20 | $0.054 | $1.08
8 | Multilayer Ceramic Capacitors MLCC - SMD/SMT 100pF +-5% 100V | 791-1206N101J101CT | 1206 SMD | 5 | $0.100 | $0.50
9 |  |  |  |  |  | $0.00
10 |  |  |  |  |  | $0.00
11 |  |  |  |  |  | $0.00
12 |  |  |  |  |  | $0.00
13 |  |  |  |  |  | $0.00
14 |  |  |  |  |  | $0.00
15 |  |  |  |  |  | $0.00
16 |  |  |  |  |  | $0.00
17 |  |  |  |  |  | $0.00
18 |  |  |  |  |  | $0.00
19 |  |  |  |  |  | $0.00
20 |  |  |  |  |  | $0.00
21 |  |  |  |  |  | $0.00
22 |  |  |  |  |  | $0.00
23 | Estimated Total |  |  |  |  | $5.97
24
25
26 | Operational Amplifiers - Op Amps Dual 15.5-V 100-kH z operational amplif A 926-LMC6042IM/NOPB | 926-LMC6042IMX/NOPB | Cut Tape | 3 | $2.75 | $8.25 | 2025-02-02
27 | Precision Amplifiers Prec CMOS Sgl Op Amp A 926-LMC6081IMX/NOPB | 926-LMC6081IN/NOPB | Through Hole | 3 | $3.07 | $9.21
28 | Thick Film Resistors - Through Hole 5000M ohms 1% | 588-SM102035007FE | Through Hole | 2 | $5.58 | $11.16
29 | Analog to Digital Converters - ADC 8-/4-Channel, +/-12V Multirange Inputs, Se | 700-MAX1033BEUP+ | Surface Mount | 1 | $15.17 | $15.17 | 2025-02-18
30 | Analog Switch ICs CMOS QUAD SPST SWITCH IC | 584-ADG212AKNZ | Through Hole | 1 | $6.69 | $6.69

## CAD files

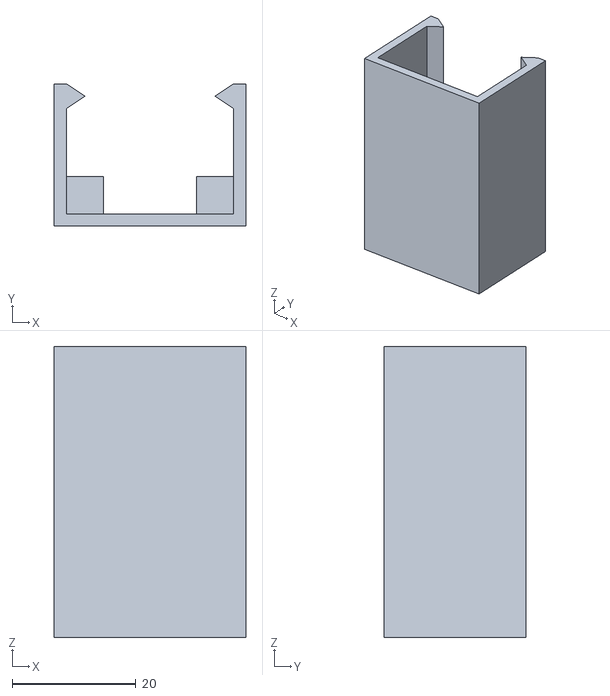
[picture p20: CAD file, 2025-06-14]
3D prints/ECE413 - BATT v1.stl
31.0 x 23.0 x 47.0

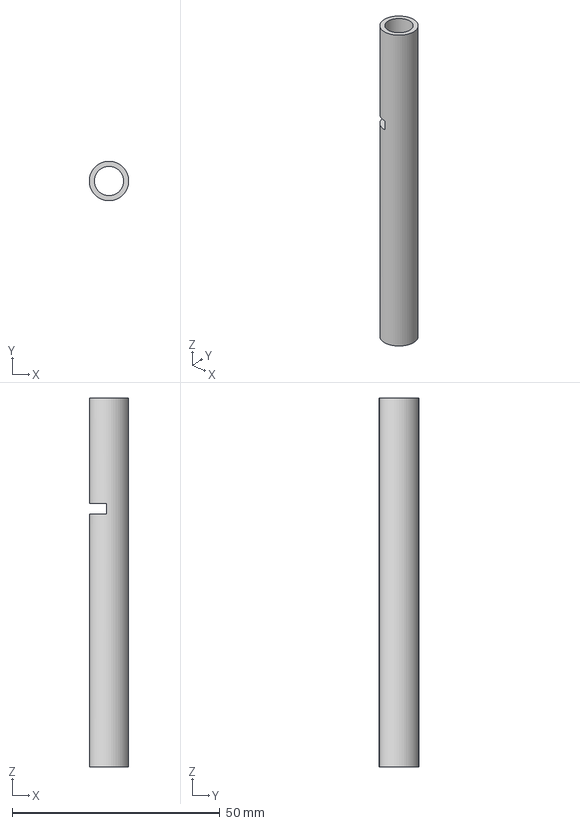
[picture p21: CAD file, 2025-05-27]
Fusion_Files/PCB Box Files Version 2/Inner_Pipe_Modified FINAL.step
9.52 x 9.52 x 88.9 mm

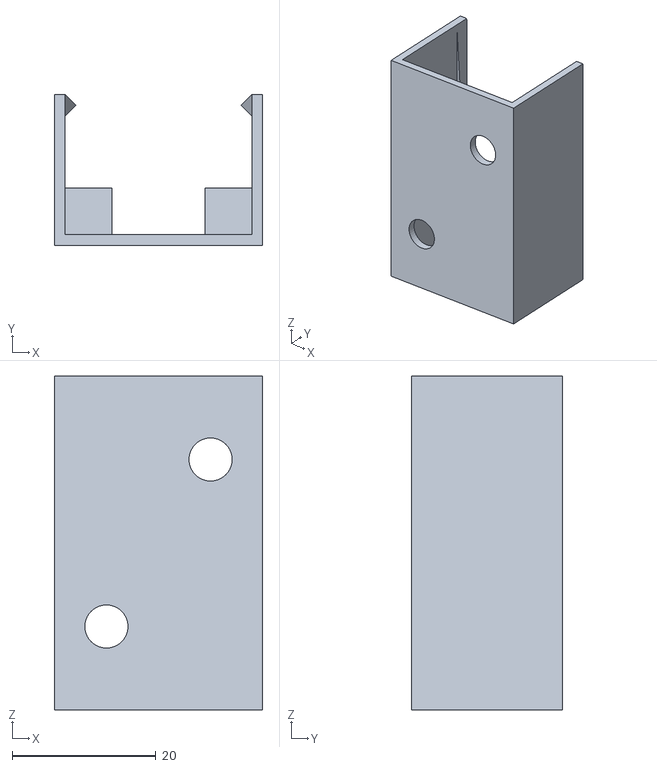
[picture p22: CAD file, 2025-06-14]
3D prints/ECE413 - BATT v2.stl
29.0 x 21.0 x 46.5

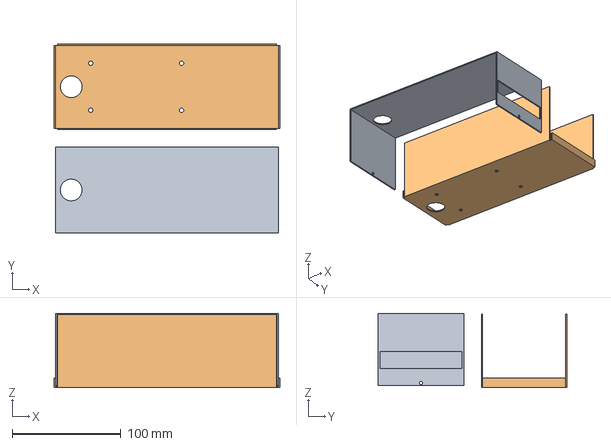
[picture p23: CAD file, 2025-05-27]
Fusion_Files/PCB Box Files Version 2/Modified LMB Chassis FINAL.step
208.0 x 174.2 x 68.5 mm

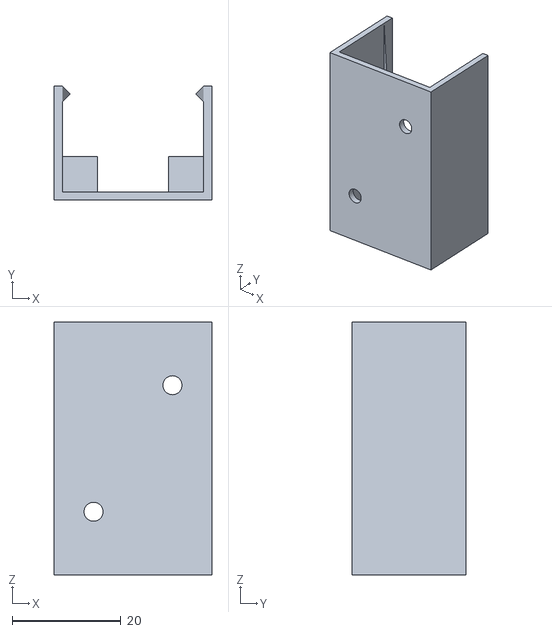
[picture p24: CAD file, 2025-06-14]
3D prints/ECE413 - BATT v3.stl
29.0 x 21.0 x 46.5

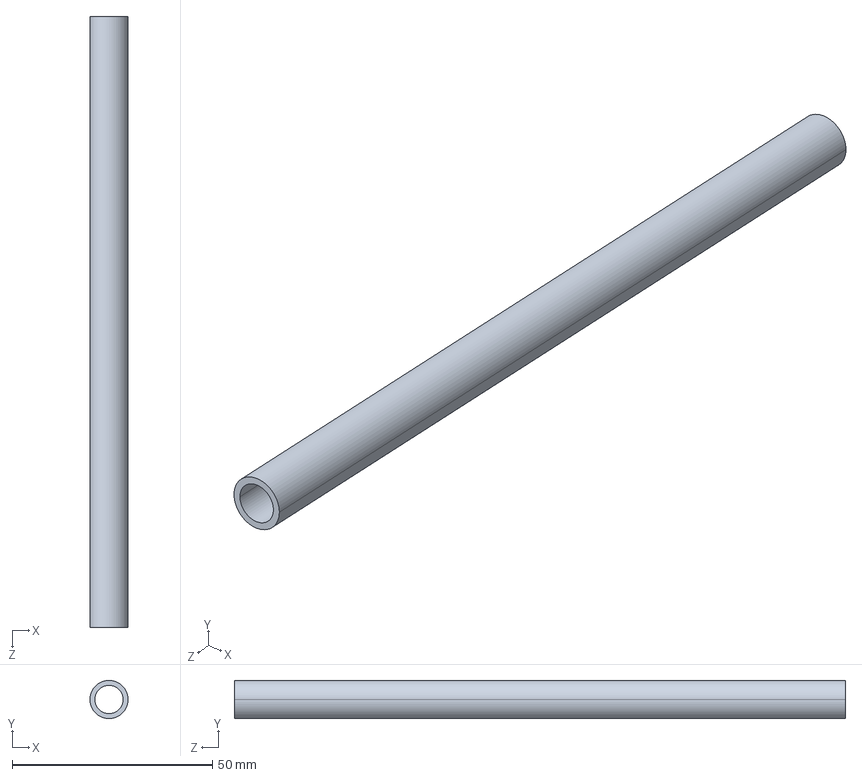
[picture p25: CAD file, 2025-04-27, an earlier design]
Fusion_Files/PCB Box Files Version 1/Inner_Pipe.STEP
9.52 x 9.52 x 152.4 mm

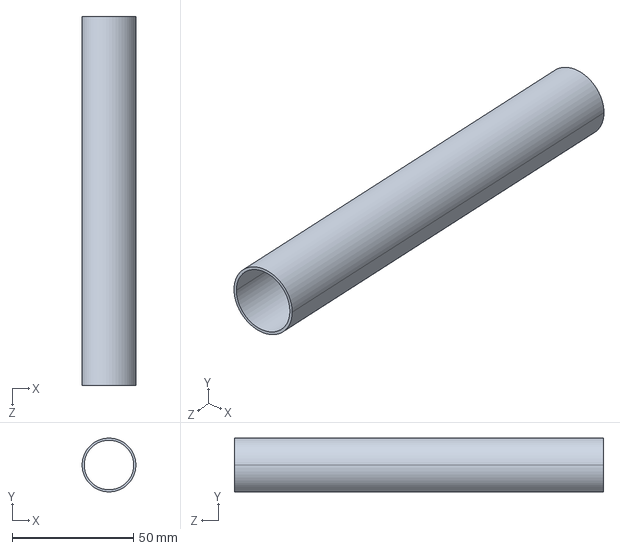
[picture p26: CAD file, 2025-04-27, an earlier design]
Fusion_Files/PCB Box Files Version 1/Outer_Pipe.STEP
22.2 x 22.2 x 152.4 mm

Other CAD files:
Fusion_Files/PCB Box Files Version 1/PCB+BOX+V2.f3d
Fusion_Files/PCB Box Files Version 1/PCB+Box+V1.f3d

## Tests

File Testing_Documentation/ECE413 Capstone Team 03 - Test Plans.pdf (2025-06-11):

# Team 03 Test Plan

2025/06/05

## Top Down Test Plan v2.1

Date of Test: | 2025/06/25
Tester: | All

Purpose
To test the entire system against its requirements by performing a top-down test.

Equipment Needed
- System Equipment
- Populated Electrostatic Dust Analyzer PCB
- 9V Battery
- USB-A to USB-C Cable
- Test Equipment
- 9V Battery
- Arduino IDE
- Laptop for Data Viewing
- Dust Particles
- Hollow Glass Pipe
- Other Equipment
- N/A

Pre-Test Setup
1. Open the Arduino IDE on laptop intended for data viewing
2. Unscrew the battery compartment from the PCB enclosure
3. Connect laptop running the Arduino IDE to the QT PY via USB-A to USB-C Cable
4. Upload <EDA_CODE_FINAL> to the QT PY
5. Establish a WiFi connection between the QT PY and the laptop running the Arduino IDE (See user manual for how to establish this connection)
6. Open the website using the generated IP address for data observation
7. Disconnect the laptop from the QT PY
8. Reattach the battery compartment

Test Steps
1. Insert the 9V battery into the battery compartment and connect it to the circuit via the battery port
2. Screw the lid back down onto the PCB enclosure
3. Insert dust particles into the hollow glass pipe
4. Position the hollow glass pipe above the faraday tube entrance (small hole on the lid)
5. Slowly pour a small amount of the dust particles out of the glass tube and let them fall into the faraday tube entrance. Pause for about 2 seconds after about half a second of pouring to allow for the sensor to return to the noise floor, then pour for another half second. Repeat this process until there are no dust particles left in the tube
6. Observe the circuit output on the website
7. Voltage output, charge value, gain, charge sign, and estimated particle size should be observed on the server

Post-Test Teardown
1. Lift the PCB enclosure up off of the testing surface
2. Brush the particles that fell through the sensor and onto the testing surface back into the container of dust particles.
3. Place the PCB enclosure back down and unscrew the lid
4. Disconnect the 9V battery from the device
5. Clean out any dust particles inside the enclosure

Top-down Test Plan Conclusions / Discussion
After running the test, we should observe that the output voltage changes de-pending on the electric charge measured at the input. Using this information, we should be able to determine the size and charge of the particles.

# Team 03 COATL Aircraft Particle Sensor

# First Test Cases using Dust (Version G Tests Created 6/5/25)

Test Author: Felix Moss

Test Case Name: | Full Operation Test | Test ID #: | 001
Description: | To test the entire system against its requirements by performing a top-down test. | Type: | ✓ white box □ black box □ _____________

Tester Information

Name of Tester: | Eisa Alsharifi | Date: | 6/05/2025
HW/SW Version: | Version G | Time: | 3:15 PM
Setup: | 1. Insert the 9V battery into the battery compartment and connect it to the circuit via the battery port
2. Screw the lid back down onto the PCB enclosure
3. Insert dust particles into the hollow glass pipe
4. Position the hollow glass pipe above the faraday tube entrance (small hole on the lid)
5. Slowly pour a small amount of the dust particles out of the glass tube and let them fall into the faraday tube entrance. Pause for about 2 seconds after about half a second of pouring to allow for the sensor to return to the noise floor, then pour for another half second. Repeat this process until there are no dust particles left in the tube
6. Observe the circuit output on the website
7. Voltage output, charge value, gain, charge sign, and estimated particle size should be observed on the server

T
E
S
T
INPUTS | EXPECTED OUTPUTS | P A S S

F
A
I
L

N
/A

Comments

1 | Slowly pour the standardized dust particles on the ramp and let them fall into the faraday tube entrance. Observe the circuit output on the website | Voltage output, charge value, gain, charge sign, and estimated particle size should be observed on the server. The range of the voltage should be between -4V and 5V, and the range of the charge should be in the 1.5fA to 1nA range. | ✓
| Overall test result: | | ✓

# Bottom Up Test Cases (Version F Tests Created 4/24/25)

Test Author: Felix Moss

Test Case Name: | Full Operation Test | Test ID #: | 001
Description: | To test the entire system against its requirements by performing a top-down test. | Type: | ✓ white box □ black box □ _____________

Tester Information

| Name of Tester: | Eisa Alsharifi | Date: | 4/24/2025
| HW/SW Version: | Version F | Time: | 3:15 PM
| Setup: | Set 1 channel on the power supply to 9V and the other to 4.5V. Connect power supply channels to the breadboard in the appropriate places. Connect laptop running Arduino IDE to the QT PY Connect oscilloscope probes to the op amp output Double check all connections
T E S T | INPUTS | EXPECTED OUTPUTS | P A S S | F A I L | N /A | Comments

1 | Move source of static electricity close to input wire | As it gets closer to the wire, there is increased charge and deviations from the 4.5V. We should see voltage variations on the oscilloscope. | ✓ | Changes were observed on both the oscilloscope and the Arduino IDE
| Overall test result: | | ✓ | Our circuit works well

Test Information
| Name of Testers: | Nathan Truong, Felix Moss, Annika Boyd, Eisa Alsharifi | Date:
| HW/SW Version: | Version F | Time:
| Setup: | Connect power supply and oscilloscope to test points on the breadboard circuit. Probes for the oscilloscope are set at the frequency input and the output. Set Power supply to 9V and 0.1A. Set the function generator to a SQUARE wave with amplitude 20mVpp, offset 0, frequency 100Hz. (The current entering the coulomb-meter is about 20pA for these tests)
S T E P | Action | Expected Result | P A S S | F A I L | N / A | Comments
1 | Test virtual ground | Both sides of the virtual ground should be around 4.5V
2 | Turn on the power and function generator. | No shorts should be evident on the power supply
3 | Probe the function generator output | A clear pulse wave (probes at function generator output) should be visible
4 | Upload code to microcontroller via Arduino IDE | Code should be successfully uploaded to the microcontroller
5 | Give the ADC a direct supply of voltage (0V - 10V in 1mV | We get matching ADC bit readings on the Arduino IDE.

| increments)
6 | Give a 2.4V signal to the gates of the analog switch from the microcontroller | The output of the switch the output should match the input
7 | Probe the amplified coulomb-meter output (LM662 op amp output) | A voltage reading of between 4V and 8V
| Overall test result:

# Breadboard Test Cases (Version A Tests from 2/19/25)

Test Author: Felix

Test Case Name: | Input Testing | Test ID #: | 1-1
Description: | Imitating the charged particles entering the device via a pulse wave to produce an amplified voltage output. | Type: | ✅ white box □ black box □ ________

Tester Information
| Name of Tester: | Nathan Truong, Eisa Alsharifi | Date: | 2/19/25
| HW/SW Version: | Version A | Time: | 2:38 PM
| Setup: | Connect power supply and oscilloscope to test points on the breadboard circuit. Probes for the oscilloscope are set at the frequency input and the output. Set Power supply to 9V and 0.1A. Set the function generator to a PULSE wave with amplitude 10mV, offset 0, frequency 1kHz. (The current entering the coulomb-meter is about 20pA for these tests)
S T E P | Action | Expected Result | P A S S | F A I L | N / A | Comments
1 | Turn on the power and | No shorts should be evident on the power supply | ✅

| function generator.
2 | Probe the function generator output | A clear pulse wave (probes at function generator output) should be visible | ✅
3 | Probe the amplified coulomb-meter output | A voltage reading of between 4V to 8V | | ❌ | Oscilloscope displays nothing on the amplified coulomb-meter output
| Overall test result: | | | ❌ | Oscilloscope displays nothing on the coulomb-meter output. Need to debug circuit and measurements.

Test Author: Felix

Test Case Name: | Input Testing | Test ID #: | 1-2
Description: | Second attempt at imitating the charged particles entering the device via a square wave to produce an amplified voltage output. Changed to SQUAREwave and Increased the wave amplitude to 100mV | Type: | ✅ white box □ black box □ ________

Tester Information
Name of Tester: | Nathan Truong, Eisa Alsharifi | Date: | 2/19/25

| HW/SW Version: | Version A | Time: | 2:55 PM
| Setup: | Connect power supply and oscilloscope to test points on the breadboard circuit. Probes for the oscilloscope are set at the frequency input and the output. Set Power supply to 9V and 0.1A. Set the function generator to a SQUARE wave with amplitude 100mVpp, offset 0, frequency 100Hz. (The current entering the coulomb-meter is about 20pA for these tests)
S T E P | Action | Expected Result | P A S S | F A I L | N / A | Comments
1 | Turn on the power and function generator. | No shorts should be evident on the power supply | ✅
2 | Probe the function generator output | A clear pulse wave (probes at function generator output) should be visible | ✅
3 | Probe the amplified coulomb-meter output | A voltage reading of between 4V to 8V | | ❌ | | Oscilloscope displayed a straight line around 0.5V
| Overall test result: | | | ❌ | | Oscilloscope displayed a straight line around 0.5V.

Test Author: Felix

Test Case Name: | Input Testing | Test ID #: | 1-3
Description: | Third attempt at imitating the charged particles entering the device via a SQUARE wave to produce an amplified voltage output. | Type: | ✅ white box □ black box □ ________

Tester Information
Name of Tester: | Nathan Truong, Eisa Alsharifi | Date: | 2/19/25

| HW/SW Version: | Version A | Time: | 3:10 PM
| Setup: | Connect power supply and oscilloscope to test points on the breadboard circuit. Probes for the oscilloscope are set at the frequency input and the output. Set Power supply to 9V and 0.1A. Set the function generator to a SQUARE wave with amplitude 100mVpp, offset 0, frequency 100Hz. (The current entering the coulomb-meter is about 20pA for these tests)
S T E P | Action | Expected Result | P A S S | F A I L | N / A | Comments
1 | Turn on the power and function generator. | No shorts should be evident on the power supply | ✅
2 | Probe the function generator output | A clear pulse wave (probes at function generator output) should be visible | ✅
3 | Probe the amplified coulomb-meter output | A voltage reading of between 4V to 8V | | ❌ | | Oscilloscope displayed a straight line around 0.5V
| Overall test result: | | | ❌ | | Oscilloscope displayed a straight line around 0.5V. Going to change oscilloscopes and test the virtual ground.

Test Author: Felix

Test Case Name: | Input Testing | Test ID #: | 1-4
Description: | Fourth attempt at imitating the charged particles entering the device via a square wave to produce an amplified voltage output. Changed to different oscilloscope for quicker debugging and tested virtual ground, changed amplitude to 20mVpp. | Type: | ✅ white box □ black box □ ________

Tester Information
Name of Tester: | Nathan Truong, Eisa Alsharifi | Date: | 2/19/25

| HW/SW Version: | Version A | Time: | 3:25 PM
| Setup: | Connect power supply and oscilloscope to test points on the breadboard circuit. Probes for the oscilloscope are set at the frequency input and the output. Set Power supply to 9V and 0.1A. Set the function generator to a SQUARE wave with amplitude 20mVpp, offset 0, frequency 100Hz. (The current entering the coulomb-meter is about 20pA for these tests)
S T E P | Action | Expected Result | P A S S | F A I L | N / A | Comments
1 | Test virtual ground | Both sides of the virtual ground should be around 4.5V | ✅ | | | Both sides of the ground were operating within acceptable ranges.
2 | Turn on the power and function generator. | No shorts should be evident on the power supply | ✅
3 | Probe the function generator output | A clear pulse wave (probes at function generator output) should be visible | ✅
4 | Probe the amplified coulomb-meter output | A voltage reading of between 4V to 8V | | ❌ | | Oscilloscope displayed nothing
| Overall test result: | | | ❌ | | The Oscilloscope displayed nothing. Need to check all connections in accordance with the circuit schematic and continue debugging.

Test Author: Felix

Test Case Name: | Input Testing | Test ID #: | 1-5
Description: | Fifth attempt at imitating the charged particles entering the device via a square wave to produce an amplified voltage output. After checking connections, we discovered there is too little current coming in from the | Type: | ✅ white box □ black box

circuit being used to generate a small current. The resistor value was changed from 67M to 1G.

□ ________

Tester Information
| Name of Tester: | Nathan Truong, Eisa Alsharifi | Date: | 2/19/25
| HW/SW Version: | Version A | Time: | 4:12 PM
| Setup: | Connect power supply and oscilloscope to test points on the breadboard circuit. Probes for the oscilloscope are set at the frequency input and the output. Set Power supply to 9V and 0.1A. Set the function generator to a SQUARE wave with amplitude 20mVpp, offset 0, frequency 100Hz. (The current entering the coulomb-meter is about 20pA for these tests)
S T E P | Action | Expected Result | P A S S | F A I L | N / A | Comments
1 | Test virtual ground | Both sides of the virtual ground should be around 4.5V | ✅ | | | Both sides of the ground were operating within acceptable ranges.
2 | Turn on the power and function generator. | No shorts should be evident on the power supply | ✅
3 | Probe the function generator output | A clear pulse wave (probes at function generator output) should be visible | ✅
4 | Probe the amplified coulomb-meter output | A voltage reading of between 4V and 8V | ✅ | | | Oscilloscope displayed the expected wave output with a mean peak to peak voltage of about 4.5V
| Overall test result: | | ✅ | | | Oscilloscope displayed the expected wave output with a mean peak to peak voltage of about 4.5V

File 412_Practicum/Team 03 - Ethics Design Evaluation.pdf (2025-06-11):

# Design and Ethics Considerations

2025-06-01

Capstone Team # | 03
Capstone Name | Aircraft Sensor
Team members | Felix Moss, Annika Boyd, Eisa Alsharifi, Nathan Truong

# Part 1: Design Considerations

You are asked to first consider these issues and then decide whether they are relevant to your capstone project Specifically, you are asked to decide whether your design needs to consider:

- Public health, safety, and welfare
- Global factors
- Cultural factors
- Environmental factors
- Economic factors

it may be unlikely that your design should consider all of these, but it is very unlikely (or impossible) that it should not consider any of these. So, the first stage is for your team to consider each of these factors and decide if they are relevant to your design. Next, you should give a short explanation for each, especially for those that you think are relevant. Explain why they are relevant and how your design may address it. It is OK if your capstone doesn’t address all of these issues. You might think about how the future of this project might affect these categories, if that helps.

Did you consider various factors in the design of your project/product? Choose Yes / No / Possibly, and discuss why you did / didn’t / might have.

Consider: | Yes/No/ Possibly | Why?
Public health, safety, and welfare | Yes | Our device is intended to prevent aviation-related accidents, meaning that our focus is public safety and welfare
Global factors | Possibly | Our device can be used by all people, meaning that if our device is successful enough for production, considerations for the global market may need to be taken into consideration.
Cultural factors | No | Our device is neutral in nature. It is concerned only with taking measurements of the environment and has no impact on any particular culture or groups of people.
Environmental factors | Yes | We are inherently concerned with environmental factors because our device measures conditions present in the environment. It’s existence does not harm or benefit the environment, as it is only an observation tool
Economic factors | No | Our device costs money to produce, but it does not have any impacts on the wider national or global economy.

# Part 2: Ethics Considerations

In industry, you will have to recognize your own and your company’s ethical and professional responsibilities. Not only would you have to recognize them, but you would also have to make judgments regarding them. In this project, you are asked to only consider if there are any potential ethical problems that could come up in your device (product) but the quality of your explanations (i.e., your judgment) will not be evaluated. Please consider the impact of your capstone project in these contexts:

- Global
- Economic
- Environmental
- Societal

Did you consider various contexts in which ethical issues may arise in the design of your project/product? Choose if it’s applicable / not applicable / might be applicable, and why / why not / why it might be.

Consider a context for ethical decision-making | Applicable: Yes/No/Possibly | Why?
Global | No | Our device is neutral in nature. It is concerned only with taking measurements of the environment. There are no globally related ethical considerations regarding its design, production, or use.
Economic | No | Our device is neutral in nature. It is concerned only with taking measurements of the environment. There are no economically related ethical considerations regarding its design, production, or use.
Environmental | No | Our device is neutral in nature. It is concerned only with taking measurements of the environment. There are no environmentally related ethical considerations regarding its design, production, or use.
Societal | No | Our device is neutral in nature. It is concerned only with taking measurements of the environment. There are no societally related ethical considerations regarding its design, production, or use.

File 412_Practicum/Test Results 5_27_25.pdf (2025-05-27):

# Team 03 Test Plan

2025/04/27

## Top Down Test Plan v1.0

Date of Test: | 2025/04/24
Tester: | Eisa Alsharifi

Purpose
To test the entire system against its requirements by performing a top-down test.

Equipment Needed
- System Equipment
- Project Breadboard
- MAX1032
- LM662 Op Amp
- QT PY Chip
- Test Equipment
- Power Supply
- Oscilloscope
- Arduino IDE
- Probes
- DMM
- Other Equipment
- N/A

Pre-Test Setup
1. Set 1 channel on the power supply to 9V and the other to 4.5V.
2. Connect power supply channels to the breadboard in the appropriate places.
3. Connect laptop running Arduino IDE to the QT PY
4. Connect oscilloscope probes to the op amp output
5. Double check all connections

Top Down Test Steps
1. Turn on both power supply channels
2. Upload the code to the QT PY
3. Observe circuit output
a. If we see a match between the Arduino IDE output voltage and the oscilloscope output voltage, this indicates a successful test.

Post-Test Teardown
1. Turn off power supply channels
2. Unplug power supply connections
3. Unplug oscilloscope probes

4. Unplug QT PY from laptop

Top-down Test Plan Conclusions / Discussion
After running the test, we should observe that the output voltage should change depending on the electric charge measured at the input. Using this information, we should be able to determine the size and charge of the particles measure

# Team 03 COATL Aircraft Particle Sensor

# Bottom Up Test Cases (Version F Tests Created 4/24/25)

Test Author: Felix Moss

Test Case Name: | Full Operation Test | Test ID #: | 001
Description: | To test the entire system against its requirements by performing a top-down test. | Type: | ✓ white box □ black box □ _____________

Tester Information

| Name of Tester: | Eisa Alsharifi | Date: | 4/24/2025
| HW/SW Version: | Version F | Time: | 3:15 PM
| Setup: | Set 1 channel on the power supply to 9V and the other to 4.5V. Connect power supply channels to the breadboard in the appropriate places. Connect laptop running Arduino IDE to the QT PY Connect oscilloscope probes to the op amp output Double check all connections
T E S T | INPUTS | EXPECTED OUTPUTS | P A S S | F A I L | N /A | Comments
1 | Move source of static electricity close to input wire | As it gets closer to the wire, there is increased charge and deviations from the 4.5V. We should see voltage variations on the oscilloscope. | ✓ | | | Changes were observed on both the oscilloscope and the Arduino IDE
| Overall test result: | | ✓ | | | Our circuit works well

Test Information
| Name of Testers: | Nathan Truong, Felix Moss, Annika Boyd, Eisa Alsharifi | Date:
| HW/SW Version: | Version F | Time:
| Setup: | Connect power supply and oscilloscope to test points on the breadboard circuit. Probes for the oscilloscope are set at the frequency input and the output. Set Power supply to 9V and 0.1A. Set the function generator to a SQUARE wave with amplitude 20mVpp, offset 0, frequency 100Hz. (The current entering the coulomb-meter is about 20pA for these tests)
S T E P | Action | Expected Result | P A S S | F A I L | N / A | Comments
1 | Test virtual ground | Both sides of the virtual ground should be around 4.5V
2 | Turn on the power and function generator. | No shorts should be evident on the power supply
3 | Probe the function generator output | A clear pulse wave (probes at function generator output) should be visible
4 | Upload code to microcontroller via Arduino IDE | Code should be successfully uploaded to the microcontroller
5 | Give the ADC a direct supply of voltage (0V - 10V in 1mV increments) | We get matching ADC bit readings on the Arduino IDE.
6 | Give a 2.4V signal to the gates of the analog switch from the microcontroller | The output of the switch the output should match the input
7 | Probe the amplified coulomb-meter output (LM662 | A voltage reading of between 4V and 8V

op amp output)
Overall test result:

# Bottom Up Test Cases (Version F Tests on 5/20/25)

Test Author: Felix Moss

Test Case Name: | Full Operation Test | Test ID #: | 001
Description: | To test the entire system against its requirements by performing a top-down test. | Type: | ✓ white box □ black box □ _____________

Tester Information

| Name of Tester: | Eisa Alsharifi | Date: | 5/20/2025
| HW/SW Version: | Version F | Time: | 3:15 PM
| Setup: | Set 1 channel on the power supply to 9V and the other to 4.5V. Connect power supply channels to the breadboard in the appropriate places. Connect laptop running Arduino IDE to the QT PY Connect oscilloscope probes to the op amp output Double check all connections
T E S T | INPUTS | EXPECTED OUTPUTS | P A S S | F A I L | N /A | Comments
1 | No inputs, only room noise

2 | Move source of static electricity close to input wire | As it gets closer to the wire, there is increased charge and deviations from the 4.5V. We should see voltage variations on the oscilloscope. | ✓
| Overall test result: | | ✓

Test Information
| Name of Testers: | Nathan Truong, Felix Moss, Annika Boyd, Eisa Alsharifi | Date: | 5/20/2025
| HW/SW Version: | Version F, Test 1 | Time: | 12:05PM
| Setup: | Connect power supply and oscilloscope to test points on the breadboard circuit. Probes for the oscilloscope are set at the frequency input and the output. Set the power supply to 9V and 0.2A. Set the function generator to a SINE wave with amplitude 200mVpp, offset 0, frequency 1KHz.
S T E P | Action | Expected Result | P A S S | F A I L | N / A | Comments
1 | Turn on the power and function generator. | No shorts should be evident on the power supply | ✓
2 | Test virtual ground | Both sides of the virtual ground should be around 4.5V | | ✓ | | Virtual ground not working properly. Only getting 3.2V instead of the intended 4.5V. (Not getting the 4.5V at the schematic’s ground)
3 | Probe the function generator output | A clear pulse wave (probes at function generator output) should be visible
4 | Upload code to microcontroller Code should be successfully uploaded to the microcontroller

| via Arduino IDE
5 | Give the ADC a direct supply of voltage (0V - 10V in 1mV increments) | We get matching ADC bit readings on the Arduino IDE.
6 | Give a 2.4V signal to the gates of the analog switch from the microcontroller | The output of the switch the output should match the input
7 | Probe the amplified coulomb-meter output (LM662 op amp output) | A voltage reading of between 4V and 8V
| Overall test result: | | Taking out microcontroller to test PCB by itself.

Test Information
| Name of Testers: | Nathan Truong, Felix Moss, Annika Boyd, Eisa Alsharifi | Date: | 5/20/2025
| HW/SW Version: | Version F, Test 2 | Time: | 12:24PM
| Setup: | Connect power supply and oscilloscope to test points on the breadboard circuit. Probes for the oscilloscope are set at the frequency input and the output. Set the power supply to 9V and 0.2A.
S T E P | Action | Expected Result | P A S S | F A I L | N / A | Comments
1 | Turn on the power and function generator. | No shorts should be evident on the power supply | ✓
2 | Test virtual ground | Both sides of the virtual ground should be around 4.5V | | ✓ | | Virtual ground not working properly. Only getting 3.2V instead of the intended 4.5V. (Not getting the 4.5V at the schematic’s ground)
3 | Probe the function generator | A clear pulse wave (probes at function generator output)

| output | should be visible
4 | Upload code to microcontroller via Arduino IDE | Code should be successfully uploaded to the microcontroller
5 | Give the ADC a direct supply of voltage (0V - 10V in 1mV increments) | We get matching ADC bit readings on the Arduino IDE.
6 | Give a 2.4V signal to the gates of the analog switch from the microcontroller | The output of the switch the output should match the input
7 | Probe the amplified coulomb-meter output (LM662 op amp output) | A voltage reading of between 4V and 8V
| Overall test result: | | ✓ | Checking all connections on the PCB, looking for potential shorts.

Test Information
| Name of Testers: | Nathan Truong, Felix Moss, Annika Boyd, Eisa Alsharifi | Date: | 5/20/2025
| HW/SW Version: | Version F, Test 3 | Time: | 12:40PM
| Setup: | Connect power supply and oscilloscope to test points on the breadboard circuit. Probes for the oscilloscope are set at the frequency input and the output. Set the power supply to 9V and 0.2A.
S T E P | Action | Expected Result | P A S S | F A I L | N / A | Comments
1 | Turn on the power and function generator. | No shorts should be evident on the power supply | ✓
2 | Test virtual ground | Both sides of the virtual ground should be around 4.5V | | ✓ | | Virtual ground not working properly. Only getting 3.2V instead of the intended 4.5V. Went into the Capstone lab for a

| | | | change of power supply to see if that was the issue but it was not. (Not getting the 4.5V at the schematic’s ground)
3 | Probe the function generator output | A clear pulse wave (probes at function generator output) should be visible
4 | Upload code to microcontroller via Arduino IDE | Code should be successfully uploaded to the microcontroller
5 | Give the ADC a direct supply of voltage (0V - 10V in 1mV increments) | We get matching ADC bit readings on the Arduino IDE.
6 | Give a 2.4V signal to the gates of the analog switch from the microcontroller | The output of the switch the output should match the input
7 | Probe the amplified coulomb-meter output (LM662 op amp output) | A voltage reading of between 4V and 8V
| Overall test result: | | ✓ | Power supply was not the issue, going to continue to look for issues in the circuit.

Test Information
| Name of Testers: | Nathan Truong, Felix Moss, Annika Boyd, Eisa Alsharifi | Date: | 5/20/2025
| HW/SW Version: | Version F, Test 4 | Time: | 12:40PM
| Setup: | Connect power supply and oscilloscope to test points on the breadboard circuit. Probes for the oscilloscope are set at the frequency input and the output. Set the power supply to 9V and 0.2A.
S T E P | Action | Expected Result | P A S S | F A I L | N / A | Comments

1 | Turn on the power and function generator. | No shorts should be evident on the power supply | ✓
2 | Test virtual ground | Both sides of the virtual ground should be around 4.5V | | ✓ | Virtual ground not working properly. Only getting 3.2V instead of the intended 4.5V. Went into the Capstone lab for a change of power supply to see if that was the issue but it was not. (Not getting the 4.5V at the schematic’s ground)
3 | Probe the function generator output | A clear pulse wave (probes at function generator output) should be visible
4 | Upload code to microcontroller via Arduino IDE | Code should be successfully uploaded to the microcontroller
5 | Give the ADC a direct supply of voltage (0V - 10V in 1mV increments) | We get matching ADC bit readings on the Arduino IDE.
6 | Give a 2.4V signal to the gates of the analog switch from the microcontroller | The output of the switch the output should match the input
7 | Probe the amplified coulomb-meter output (LM662 op amp output) | A voltage reading of between 4V and 8V
| Overall test result: | | | ✓ | Power supply was not the issue, going to continue to look for issues in the circuit.

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

| HW/SW Version: | Version F, Test 5 | Time: | 12:40PM
| Setup: | Connect power supply and oscilloscope to test points on the breadboard circuit. Probes for the oscilloscope are set at the frequency input and the output. Set the power supply to 9V and 0.2A.
S T E P | Action | Expected Result | P A S S | F A I L | N / A | Comments
1 | Turn on the power and function generator. | No shorts should be evident on the power supply | ✓
2 | Test virtual ground | Both sides of the virtual ground should be around 4.5V | | ✓ | | Virtual ground not working properly. Only getting 3.2V instead of the intended 4.5V. We are reading the 10k resistors in the voltage divider as 5k. This is because the resistors are mistakenly being connected in parallel.
3 | Probe the function generator output | A clear pulse wave (probes at function generator output) should be visible
4 | Upload code to microcontroller via Arduino IDE | Code should be successfully uploaded to the microcontroller
5 | Give the ADC a direct supply of voltage (0V - 10V in 1mV increments) | We get matching ADC bit readings on the Arduino IDE.
6 | Give a 2.4V signal to the gates of the analog switch from the microcontroller | The output of the switch the output should match the input
7 | Probe the amplified coulomb-meter output (LM662 op amp output) | A voltage reading of between 4V and 8V
| Overall test result: | | | ✓ | | Potential issue with the voltage divider was found. Going to test

all individual connections on the PCB to completely rule out any missed connections. Going to switch out a resistors for fresh 10k

Test Information
| Name of Testers: | Nathan Truong, Felix Moss, Annika Boyd, Eisa Alsharifi | Date: | 5/20/2025
| HW/SW Version: | Version F, Test 6 | Time: | 1:25PM
| Setup: | Connect power supply and oscilloscope to test points on the breadboard circuit. Probes for the oscilloscope are set at the frequency input and the output. Set the power supply to 9V and 0.2A.
S T E P | Action | Expected Result | P A S S | F A I L | N / A | Comments
1 | Turn on the power and function generator. | No shorts should be evident on the power supply | ✓
2 | Test virtual ground | Both sides of the virtual ground should be around 4.5V | | ✓ | | Virtual ground not working properly. Only getting 3.2V instead of the intended 4.5V.
3 | Probe the function generator output | A clear pulse wave (probes at function generator output) should be visible
4 | Upload code to microcontroller via Arduino IDE | Code should be successfully uploaded to the microcontroller
5 | Give the ADC a direct supply of voltage (0V - 10V in 1mV increments) | We get matching ADC bit readings on the Arduino IDE.
6 | Give a 2.4V signal to the gates of the analog switch from the microcontroller | The output of the switch the output should match the input

7 | Probe the amplified coulomb-meter output (LM662 op amp output) | A voltage reading of between 4V and 8V
| Overall test result: | | ✓ | Still not working. Going to change out the buffer for a new one since we identified that it was not getting enough input voltage.

Test Information
| Name of Testers: | Nathan Truong, Felix Moss, Annika Boyd, Eisa Alsharifi | Date: | 5/20/2025
| HW/SW Version: | Version F, Test 6 | Time: | 2:53PM
| Setup: | Connect power supply and oscilloscope to test points on the breadboard circuit. Probes for the oscilloscope are set at the frequency input and the output. Set the power supply to 9V and 0.2A.
S T E P | Action | Expected Result | P A S S | F A I L | N / A | Comments
1 | Turn on the power and function generator. | No shorts should be evident on the power supply | ✓
2 | Test virtual ground | Both sides of the virtual ground should be around 4.5V | ✓ | | | Buffer was the issue! Virtual ground is working properly now.
7 | Probe the amplified coulomb-meter output (LM662 op amp output) | A voltage reading of between 4V and 8V with responses to outside sources of charged particles | ✓ | | | We have a stable DC output of 4.5V and the output is affected by outside interference sources as intended.
| Overall test result: | | | ✓ | | The PCB is now functioning as intended. We believe the problem was that when a capacitor was popped, the buffer was burnt by

the surge of current.

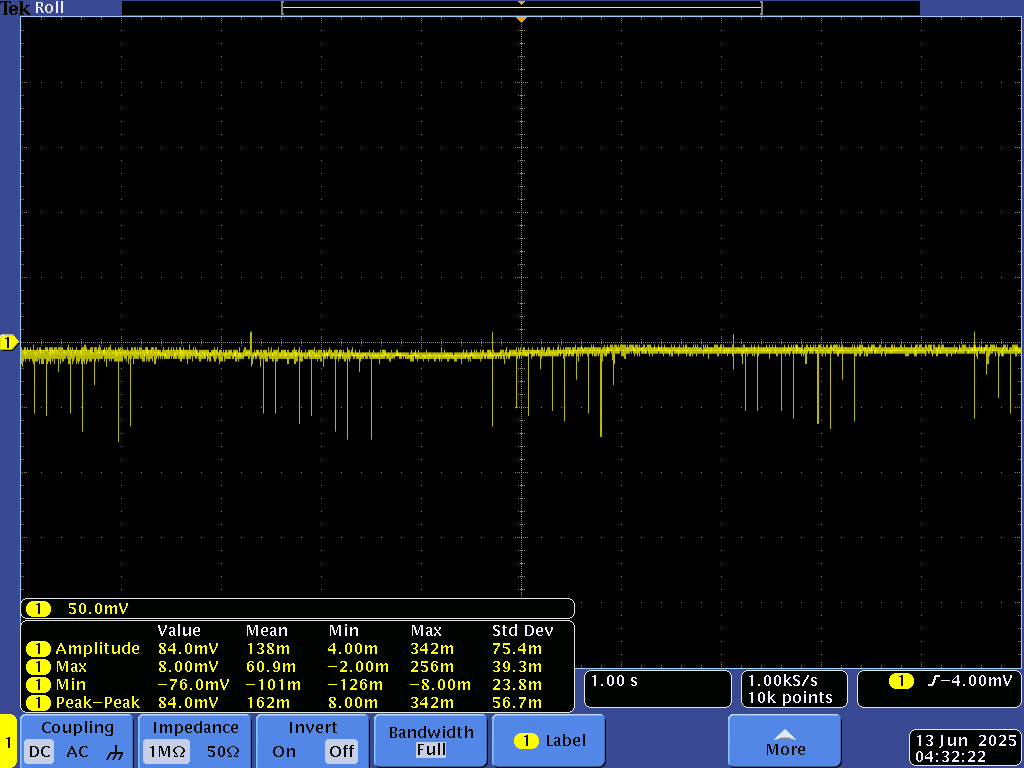
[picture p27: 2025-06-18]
Test Data/gnd_wifioff.png

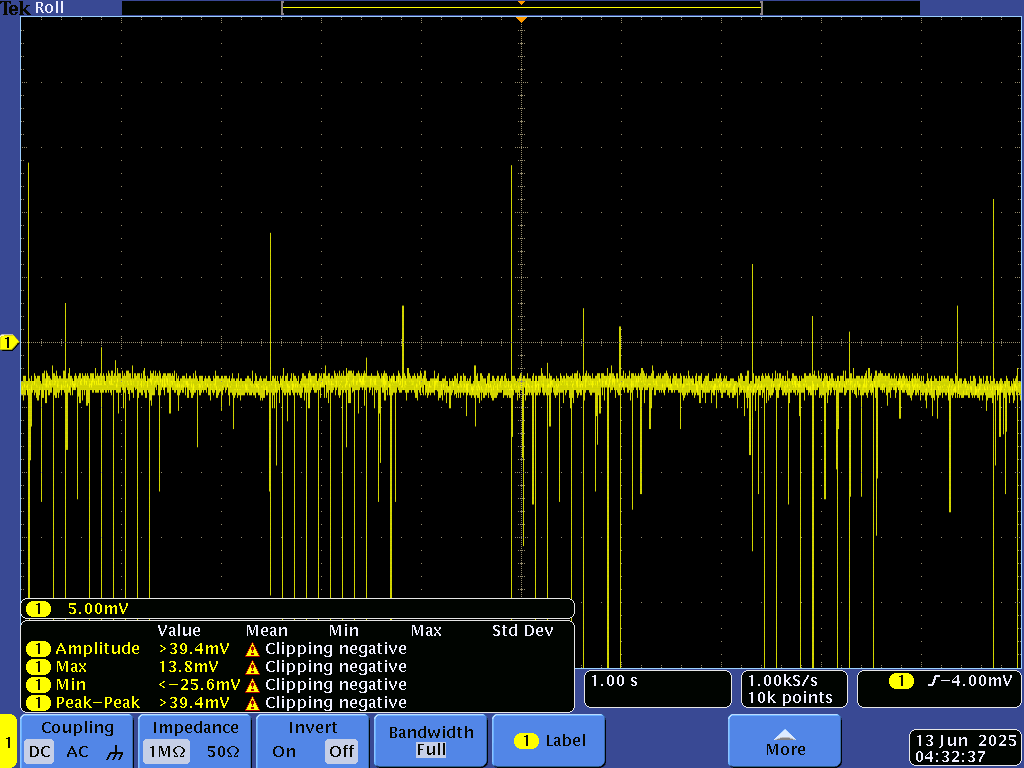
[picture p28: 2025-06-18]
Test Data/gnd_wifioff2.png

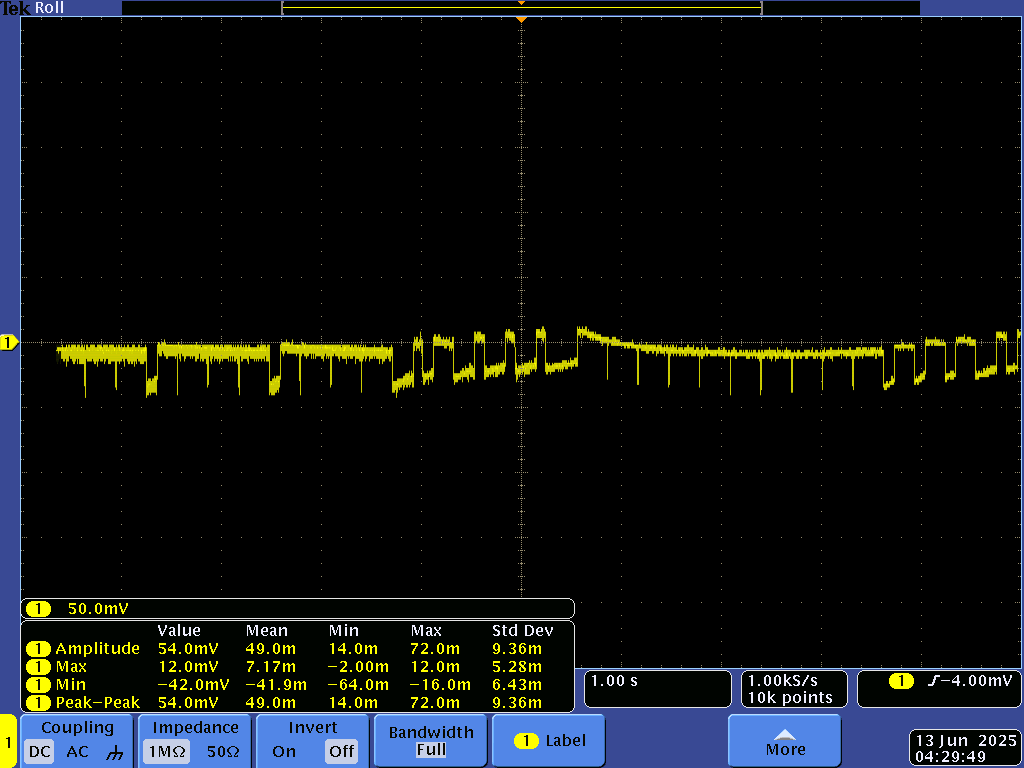
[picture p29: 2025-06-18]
Test Data/gnd_wifion.png

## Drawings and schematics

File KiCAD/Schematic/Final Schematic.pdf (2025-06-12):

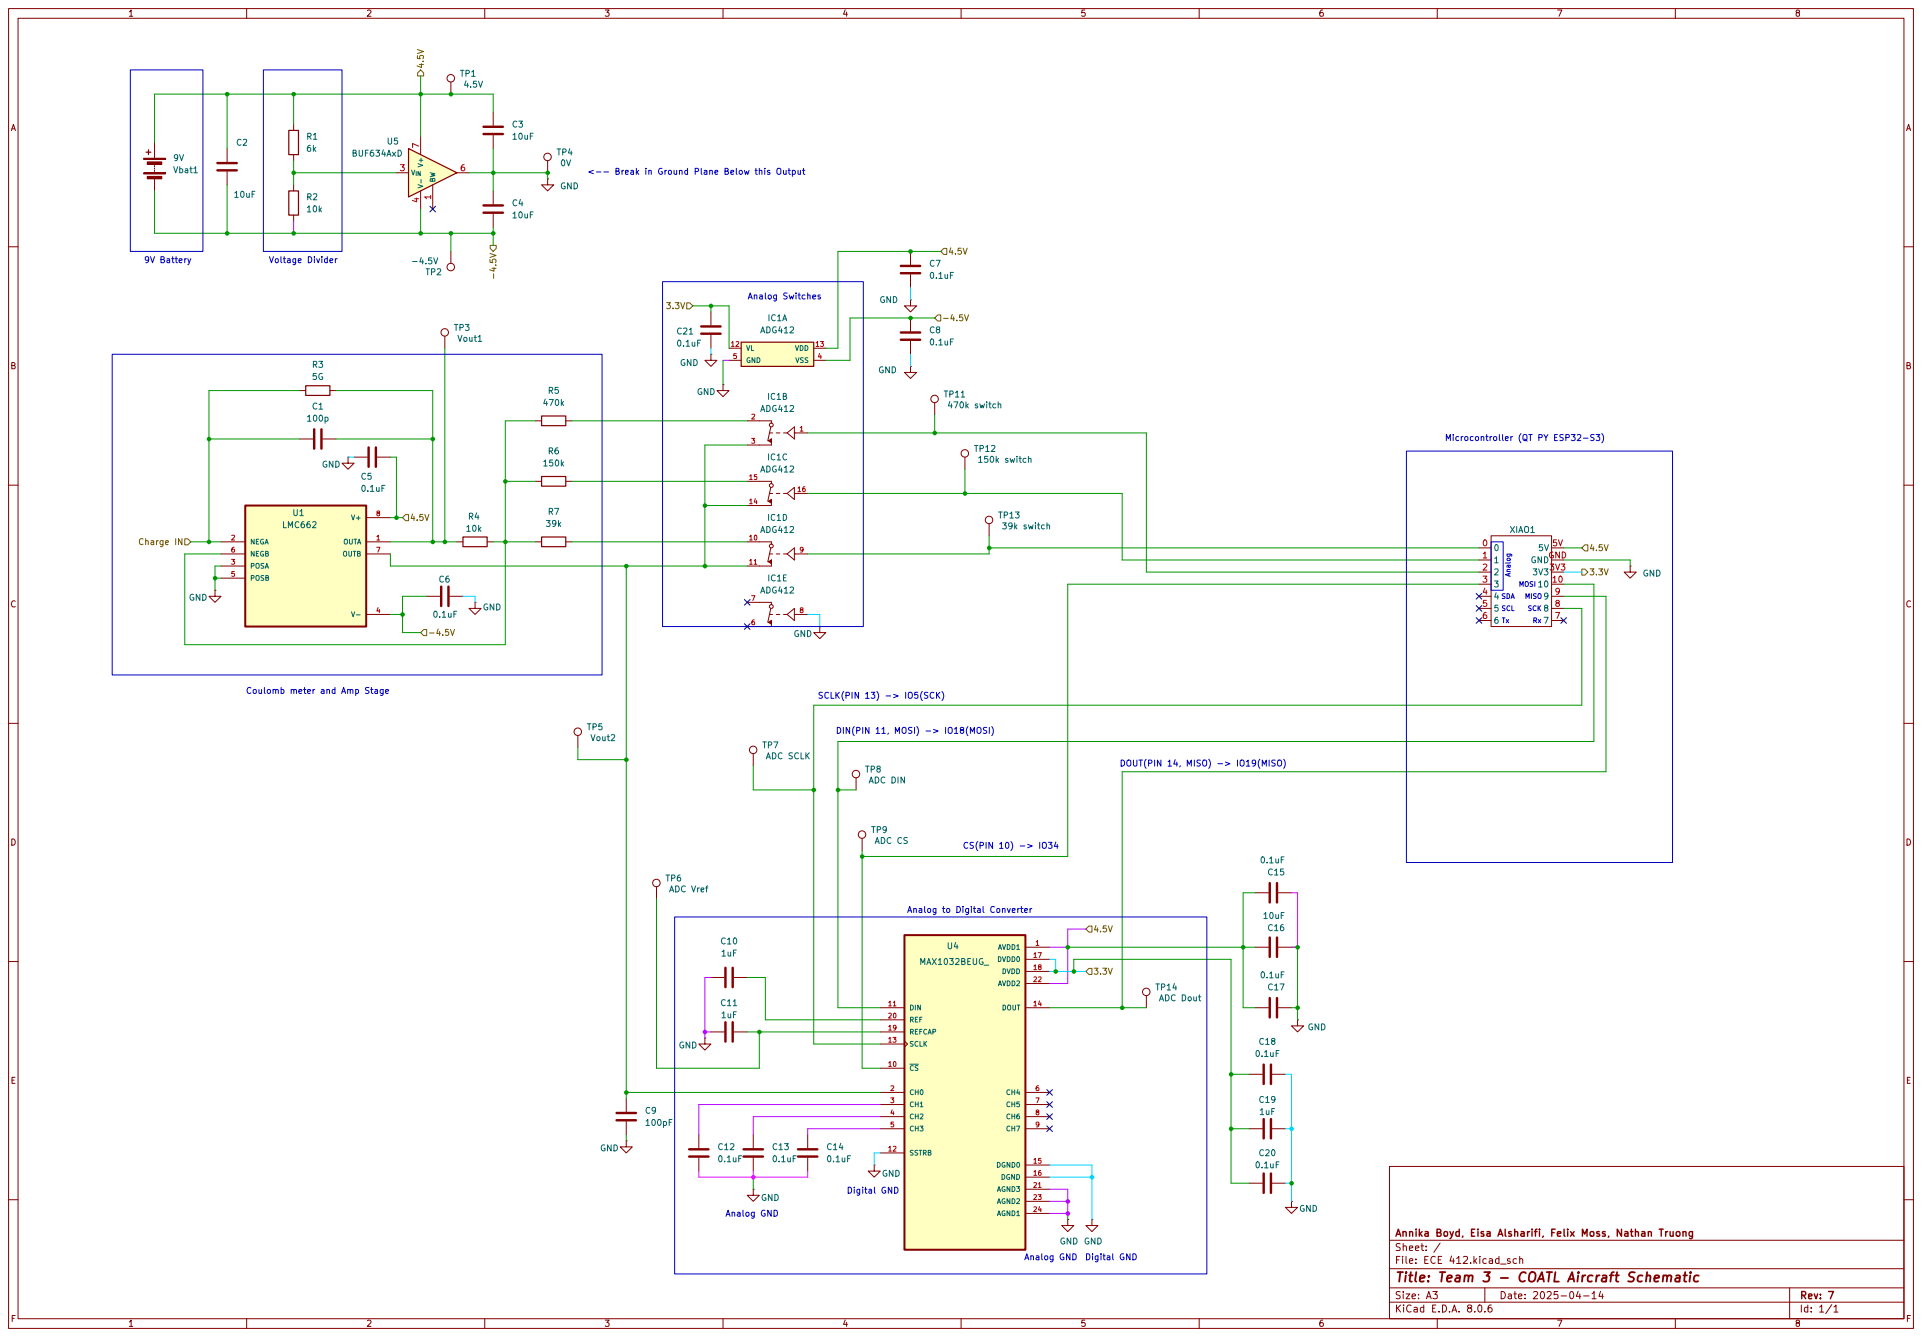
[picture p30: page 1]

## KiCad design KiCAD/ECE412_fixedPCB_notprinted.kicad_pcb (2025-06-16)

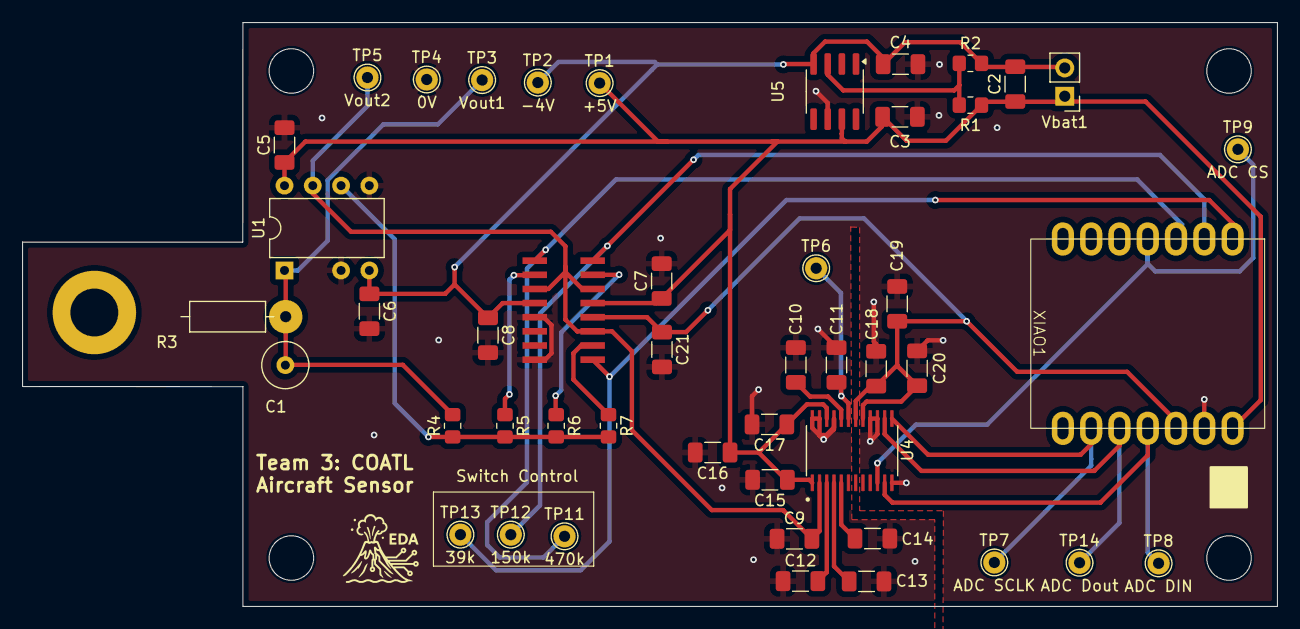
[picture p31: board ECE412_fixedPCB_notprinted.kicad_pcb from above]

Board: 2 copper layers, 112.7 x 52.4 mm, 47 parts (0 on the bottom side), 23 nets.

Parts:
C1: 100p; C_Radial_D10.0mm_H12.5mm_P5.00mm
C2, C3, C4, C16: 10uF; C_1206_3216Metric_Pad1.33x1.80mm_HandSolder
C5, C6, C7, C8, C12, C13, C14, C15, C17, C18, C20, C21: 0.1uF; C_1206_3216Metric_Pad1.33x1.80mm_HandSolder
C9: 100pF; C_1206_3216Metric_Pad1.33x1.80mm_HandSolder
C10, C11, C19: 1uF; C_1206_3216Metric_Pad1.33x1.80mm_HandSolder
IC1: ADG412; SOIC16N
R1, R4: 10k; R_0805_2012Metric_Pad1.20x1.40mm_HandSolder
R2: 6k; R_0805_2012Metric_Pad1.20x1.40mm_HandSolder
R3: 5G; R_Vishay_TR10X5G00JNES
R5: 470k; R_0805_2012Metric_Pad1.20x1.40mm_HandSolder
R6: 150k; R_0805_2012Metric_Pad1.20x1.40mm_HandSolder
R7: 39k; R_0805_2012Metric_Pad1.20x1.40mm_HandSolder
TP1: +5V; TestPoint_THTPad_D2.0mm_Drill1.0mm
TP2: -4V; TestPoint_THTPad_D2.0mm_Drill1.0mm
TP3: Vout1; TestPoint_THTPad_D2.0mm_Drill1.0mm
TP4: 0V; TestPoint_THTPad_D2.0mm_Drill1.0mm
TP5: Vout2; TestPoint_THTPad_D2.0mm_Drill1.0mm
TP6: ADC Vref; TestPoint_THTPad_D2.0mm_Drill1.0mm
TP7: ADC SCLK; TestPoint_THTPad_D2.0mm_Drill1.0mm
TP8: ADC DIN; TestPoint_THTPad_D2.0mm_Drill1.0mm
TP9: ADC CS; TestPoint_THTPad_D2.0mm_Drill1.0mm
TP11: 470k; TestPoint_THTPad_D2.0mm_Drill1.0mm
TP12: 150k; TestPoint_THTPad_D2.0mm_Drill1.0mm
TP13: 39k; TestPoint_THTPad_D2.0mm_Drill1.0mm
TP14: ADC Dout; TestPoint_THTPad_D2.0mm_Drill1.0mm
U1: LMC662; DIP-8_W7.62mm
U4: MAX1032BEUG_; SOP65P640X110-24N
U5: BUF634AxD; SOIC-8_3.9x4.9mm_P1.27mm
Vbat1: 9V; PinHeader_1x02_P2.54mm_Vertical
XIAO1: XIAO_QTpy

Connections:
/3.3V: C18.2, C19.1, C20.2, C21.1, IC1.12 (VL), U4.17 (DVDD0), U4.18 (DVDD), XIAO1.3V3
/+5V: C2.1, C3.1, C5.1, C7.1, C15.1, C16.1, C17.1, IC1.13 (VDD), R1.1, TP1.1, U1.8 (V+), U4.1 (AVDD1), U4.22 (AVDD2), U5.7 (V+), Vbat1.1 (+), XIAO1.5V
/-4V: C2.2, C4.2, C6.1, C8.1, IC1.4 (VSS), R2.2, TP2.1, U1.4 (V-), U5.4 (V-), Vbat1.2 (-)
GND: C3.2, C4.1, C5.2, C6.2, C7.2, C8.2, C9.1, C10.1, C11.2, C12.1, C13.1, C14.1, C15.2, C16.2, C17.2, C18.1, C19.2, C20.1, C21.2, IC1.5 (GND), IC1.8, TP4.1, U1.3 (POSA), U1.5 (POSB), U4.12 (SSTRB), U4.15 (DGND0), U4.16 (DGND), U4.21 (AGND3), U4.23 (AGND2), U4.24 (AGND1), U5.6, XIAO1.GND
unnamed: IC1.1, TP11.1, XIAO1.2
unnamed: IC1.2, R5.1
unnamed: IC1.9, TP13.1, XIAO1.0
unnamed: IC1.10, R7.1
unnamed: IC1.15, R6.1
unnamed: IC1.16, TP12.1, XIAO1.1
unnamed: R4.1, R5.2, R6.2, R7.2, U1.6 (NEGB)
unnamed: C1.1, R3.1, R4.2, TP3.1, U1.1 (OUTA)
unnamed: C9.2, IC1.3, IC1.11, IC1.14, TP5.1, U1.7 (OUTB), U4.2 (CH0)
unnamed: C12.2, U4.3 (CH1)
unnamed: C13.2, U4.4 (CH2)
unnamed: C14.2, U4.5 (CH3)
unnamed: TP8.1, U4.11 (DIN), XIAO1.10
unnamed: TP14.1, U4.14 (DOUT), XIAO1.9
unnamed: C10.2, U4.20 (REF)
unnamed: C11.1, TP6.1, U4.19 (REFCAP)
unnamed: TP7.1, U4.13 (SCLK), XIAO1.8
unnamed: TP9.1, U4.10 (~CS), XIAO1.3
unnamed: R1.2, R2.1, U5.3 (V_{IN})

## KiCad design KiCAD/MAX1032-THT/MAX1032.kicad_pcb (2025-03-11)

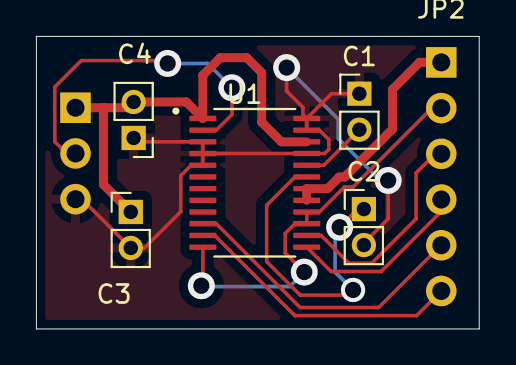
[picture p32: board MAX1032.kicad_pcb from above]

Board: 2 copper layers, 24.6 x 16.2 mm, 7 parts (0 on the bottom side), 11 nets.

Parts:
C1, C3: 0.1uF; PinHeader_1x02_P2.00mm_Vertical
C2: 1uF; PinHeader_1x02_P2.00mm_Vertical
C4: 10uF; PinHeader_1x02_P2.00mm_Vertical
JP1: HEADER-1X3; PinHeader_1x03_P2.54mm_Horizontal
JP2: HEADER-1X6; PinHeader_1x06_P2.54mm_Horizontal
U1: MAX1032BEUG_; SOP65P640X110-24N

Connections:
/AVDD: C3.1, C4.2, JP1.1, U1.1 (AVDD1), U1.22 (AVDD2)
/CH0: JP1.2, U1.2 (CH0)
/CS*: JP2.5, U1.10 (~CS)
/DGND: JP2.2, U1.12 (SSTRB), U1.15 (DGND0), U1.16 (DGND)
/DIN: JP2.6, U1.11 (DIN)
/DOUT: JP2.3, U1.14 (DOUT)
/DVDD: JP2.1, U1.17 (DVDD0), U1.18 (DVDD)
/SCLK: JP2.4, U1.13 (SCLK)
GND: C1.1, C2.2, C3.2, C4.1, JP1.3, U1.3 (CH1), U1.4 (CH2), U1.5 (CH3), U1.21 (AGND3), U1.23 (AGND2), U1.24 (AGND1)
unnamed: C1.2, U1.20 (REF)
unnamed: C2.1, U1.19 (REFCAP)

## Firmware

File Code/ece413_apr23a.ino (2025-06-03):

#include <SPI.h>
#include <WiFi.h>
#include <WebServer.h>

// === WiFi Configuration ===
const char* ssid = "Etherium";
const char* password = "ladylink";

WebServer server(80);

// === Pin Configuration ===
#define GAIN1_PIN 18
#define GAIN2_PIN 17
#define GAIN3_PIN 9
#define CS_PIN     8
#define SPI_SCK    36
#define SPI_MOSI   35
#define SPI_MISO   37

// === Constants ===
#define V_REF       4.098
//#define VIRTUAL_GND 4.0
#define MAX_ADC     16383
#define V_ADC_MAX   (3 * V_REF)
#define FEEDBACK_CAP 1e-10

// === Globals ===
bool manualGain = false;
int activeGain = 1;
uint16_t adcRaw = 0;
float voltage = 0.0, charge = 0.0;
String gainLabel = "Gain 1 (3.9x)";
String chargeStr = "";
String chargeSign = "";
float testVoltage = 4.5;
bool testMode = true, clippingWarning = false;

// === Serial Log ===
constexpr uint16_t LOG_DEPTH = 120;
String logBuf[LOG_DEPTH];
uint16_t logHead = 0;

void addLogLine(const String& ln) {
  logBuf[logHead] = ln;
  logHead = (logHead + 1) % LOG_DEPTH;
}

void handleLog() {
  String out;
  for (uint16_t i = 0; i < LOG_DEPTH; ++i) {
    uint16_t idx = (logHead + i) % LOG_DEPTH;
    if (logBuf[idx].length()) out += logBuf[idx] + "\n";
  }
  server.send(200, "text/plain", out);
}

// === Gain Switching ===
void setGain(int g) {
  digitalWrite(GAIN1_PIN, g == 1);
  digitalWrite(GAIN2_PIN, g == 2);
  digitalWrite(GAIN3_PIN, g == 3);
  activeGain = g;
  gainLabel = (g == 1) ? "Gain 1 (3.9x)" : (g == 2) ? "Gain 2 (15x)" : "Gain 3 (47x)";
}

void detectGain(float deltaV) {
  if (!manualGain) {
    if (abs(deltaV) <= 0.2) setGain(3);
    else if (abs(deltaV) <= 0.6) setGain(2);
    else setGain(1);
  }
  chargeSign = (deltaV >= 0) ? "+" : "-";
}

uint16_t readMAX1032() {
  uint8_t r[3] = {0};
  digitalWrite(CS_PIN, LOW);
  SPI.transfer(0b10000000);
  r[0] = SPI.transfer(0x00);
  r[1] = SPI.transfer(0x00);
  r[2] = SPI.transfer(0x00);
  digitalWrite(CS_PIN, HIGH);
  return (((r[1] << 8) | r[2]) >> 2) & 0x3FFF;
}

void calculateDerivedValues() {
  adcRaw = testMode ? (uint16_t)((testVoltage / V_ADC_MAX) * MAX_ADC + 0.5) : readMAX1032();
  voltage = (adcRaw / (float)MAX_ADC) * V_ADC_MAX;
  float deltaV = voltage /*- VIRTUAL_GND*/;
  detectGain(deltaV);
  charge = deltaV * FEEDBACK_CAP;
  chargeStr = chargeSign + String(abs(charge) * 1e12, 4) + " pC";
  clippingWarning = (voltage > /*VIRTUAL_GND +*/ 4.75);
}

// === Particle Estimates ===
String particleEstimate(float q, String t) {
  float minS, maxS;
  if (t == "Volcanic Ash") { minS = 1e-6; maxS = 1e-5; }
  else if (t == "Wildfire Smoke") { minS = 1e-8; maxS = 1e-6; }
  else if (t == "Mineral Dust") { minS = 7.7e-7; maxS = 2.34e-6; }
  else return "";

  float dMin = 2 * sqrt(abs(q) / (4 * PI * maxS));
  float dMax = 2 * sqrt(abs(q) / (4 * PI * minS));
  return String(t) + ": " + String(dMin * 1e6, 2) + "–" + String(dMax * 1e6, 2) + " µm";
}

// === Web Page Handlers ===
void handleMain() {
  calculateDerivedValues();
  String page = "<!DOCTYPE html><html><head><title>Dust Analyzer</title>";
  page += "<meta name='viewport' content='width=device-width, initial-scale=1.0'>";
  page += "<style>";
  page += "body{margin:0;padding:0;font-family:monospace;background:#A1A6A8;";
  page += "background-image:url('https://github.com/NathanTruong0930/COATL-AIRCRAFT/blob/main/Code/Volcano2.png?raw=true');";
  page += "background-repeat:no-repeat;background-position:center top;background-size:contain;height:auto;min-height:100vh;overflow-y:scroll;}";
  page += "#dashboard{position:absolute;top:60vh;left:50%;transform:translateX(-50%);background-color:transparent;padding:1vh;text-align:center;width:90vw;max-width:450px;font-size:2vh;}";
  page += "h1{font-size:3vh;margin:0.5vh 0;}p{font-size:2vh;margin:1vh 0;}button{font-family:monospace;background-color:#E87749;color:black;padding:1vh 2vh;border:none;cursor:pointer;font-size:2vh;margin-top:2vh;}";
  page += "</style></head><body>";
  page += "<script>window.onload=function(){document.getElementById('dashboard').scrollIntoView({behavior:'smooth',block:'center'});}</script>";
  page += "<div id='dashboard'><h1>Electrostatic Dust Analyzer</h1>";
  page += "<p><b>Charge:</b> " + chargeStr + "</p>";
  page += "<p><b>Particle Size Estimates:</b></p>";
  page += "<p>" + particleEstimate(charge, "Volcanic Ash") + "</p>";
  page += "<p>" + particleEstimate(charge, "Wildfire Smoke") + "</p>";
  page += "<p>" + particleEstimate(charge, "Mineral Dust") + "</p>";
  page += "<form action='/details'><button>Technical Details</button></form></div></body></html>";
  server.send(200, "text/html", page);
}

void handleDetails() {
  calculateDerivedValues();
  String page = "<html><head><title>Details</title>";
  page += "<meta name='viewport' content='width=device-width, initial-scale=1.0'>";
  page += "<style>body{background:#A1A6A8;color:black;font-family:monospace;padding:20px;}button{background:#E87749;color:black;font-family:monospace;padding:10px;border:none;cursor:pointer;}";
  page += ".radio-group{display:flex;gap:10px;margin-top:10px;}";
  page += "input[type=radio]{display:none;}label{padding:6px 12px;border:1px solid black;border-radius:5px;cursor:pointer;}input[type=radio]:checked+label{background:#E87749;color:black;}</style>";
  page += "<script>function upd(){fetch('/log').then(r=>r.text()).then(t=>{let p=document.getElementById('log');p.textContent=t;p.scrollTop=p.scrollHeight;});}setInterval(upd,1000);window.onload=upd;</script></head><body>";
  page += "<a href='/' style='text-decoration:none;color:black;font-weight:bold;font-size:18px;'>&#8592; Main Page</a>";
  page += "<h2>Technical Details</h2>";
  page += "<p><b>Charge:</b> " + chargeStr + "</p>";
  page += "<p><b>Voltage:</b> " + String(voltage, 4) + " V</p>";
  page += "<p><b>ADC Bits:</b> " + String(adcRaw) + "</p>";
  page += "<p><b>Gain Stage:</b> " + gainLabel + "</p>";
  if (clippingWarning) page += "<p style='color:red'><b>⚠️ Clipping risk!</b></p>";

  // Gain toggle
  page += "<form method='POST' action='/toggleGain'><button>Toggle " + String(manualGain ? "Auto" : "Manual") + " Gain</button></form>";

  // Gain selectors
  if (manualGain) {
    page += "<form method='POST' action='/selectGain'><div class='radio-group'>";
    for (int g = 1; g <= 3; g++) {
      String val = "gain" + String(g);
      String checked = (activeGain == g) ? "checked" : "";
      String label = (g == 1) ? "Gain 1 (3.9x)" : (g == 2) ? "Gain 2 (15x)" : "Gain 3 (47x)";
      page += "<input type='radio' id='" + val + "' name='gain' value='" + String(g) + "' " + checked + ">";
      page += "<label for='" + val + "'>" + label + "</label>";
    }
    page += "</div><button>Apply Gain</button></form>";
  }

  // Serial log monitor
  page += "<h3>Serial Monitor</h3><pre id='log' style='background:#000;color:#0f0;padding:8px;height:300px;overflow-y:scroll;font-family:monospace;'></pre>";
  page += "</body></html>";
  server.send(200, "text/html", page);
}

void handleToggleGain() {
  manualGain = !manualGain;
  if (!manualGain) setGain(1); // reset to auto start
  server.sendHeader("Location", "/details");
  server.send(303);
}

void handleSelectGain() {
  if (server.hasArg("gain")) {
    int g = server.arg("gain").toInt();
    if (g >= 1 && g <= 3) setGain(g);
  }
  server.sendHeader("Location", "/details");
  server.send(303);
}

void setup() {
  Serial.begin(115200);
  SPI.begin(SPI_SCK, SPI_MISO, SPI_MOSI);
  pinMode(CS_PIN, OUTPUT); digitalWrite(CS_PIN, HIGH);
  pinMode(GAIN1_PIN, OUTPUT);
  pinMode(GAIN2_PIN, OUTPUT);
  pinMode(GAIN3_PIN, OUTPUT);
  setGain(1);

  WiFi.begin(ssid, password);
  while (WiFi.status() != WL_CONNECTED) { delay(500); Serial.print("."); }
  Serial.println("\nWiFi connected. IP: " + WiFi.localIP().toString());

  server.on("/", handleMain);
  server.on("/details", handleDetails);
  server.on("/log", handleLog);
  server.on("/toggleGain", HTTP_POST, handleToggleGain);
  server.on("/selectGain", HTTP_POST, handleSelectGain);
  server.begin();
}

void loop() {
  server.handleClient();
  if (testMode && Serial.available()) {
    String input = Serial.readStringUntil('\n');
    input.trim();
    float entered = input.toFloat();
    if (entered >= 0.0 && entered <= V_ADC_MAX) {
      testVoltage = entered;
      Serial.println("Simulated input: " + String(testVoltage));
      addLogLine("Manual input: " + String(testVoltage));
    }
  }
}

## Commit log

2025-02-20 Update and rename Kicad/ECE 412-B_Adhesive.gbr to Kicad/Gerber Files/ECE 412-B_Adhesive.gbr
    [ECE 412-B_Adhesive.gbr]
2025-03-18 Updated weekly progress report, Added team meeting and team check-in notes, Added fusion files for PCB box
    [PCB+BOX+V2.f3d, PCB+Box+V1.f3d]
2025-04-27 Updated weekly progress report, Added newest fusion files, Added team meeting notes
    [Inner_Pipe.STEP, Outer_Pipe.STEP]
2025-05-27 Added final PCB Box Files
    [Inner_Pipe.STEP, Inner_Pipe_Modified FINAL.step, Modified LMB Chassis FINAL.step, Outer_Pipe.STEP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]
2025-06-11 File renaming, README modifications
    [ECE 412.kicad_pcb, ECE 412.kicad_sch, Inner_Pipe.STEP, Inner_Pipe_Modified FINAL.step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]
2025-06-16 Add files via upload
    fixed: B.Mask cutout, TP names on wrong layer
    [ECE412_fixedPCB_notprinted.kicad_pcb, ECE412_fixedPCB_notprinted.kicad_sch]
